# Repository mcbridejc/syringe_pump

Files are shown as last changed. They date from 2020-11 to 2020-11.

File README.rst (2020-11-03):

================
DIY Syringe Pump
================

A simple, cheap syringe pump designed for pumping controlled volumes of fluid
onto and off of the PurpleDrop_. It's built from 3D printed custom parts and
off-the-shelf parts from ServoCity_, with a Pololu Tic stepper controller so
that it can be plugged easily into a USB port and controlled using the drivers
from Pololu.

This design was inspired by C.A. Varnon's `open source design <http://cavarnon.com/syringepump>`_.
It's very similar, but a bit more compact, being designed for a smaller stepper
motor and smaller syringe.

The main disadvantage of the design is that there is a significant backlash,
which leads to hysteresis when changing the direction of pumping. For my
application, this is not much of a concern, as each pump will operate in
only one direction. However, it may be an issue in some cases. I think it may
be correctable with the addition of a tension spring between the end-plate and
the "sled", but I haven't tested this. It's probably necessary to get a longer
U-channel in order to accomodate the spring and still be able to actuate the full
plunger depth.

The total cost of parts is about $100.

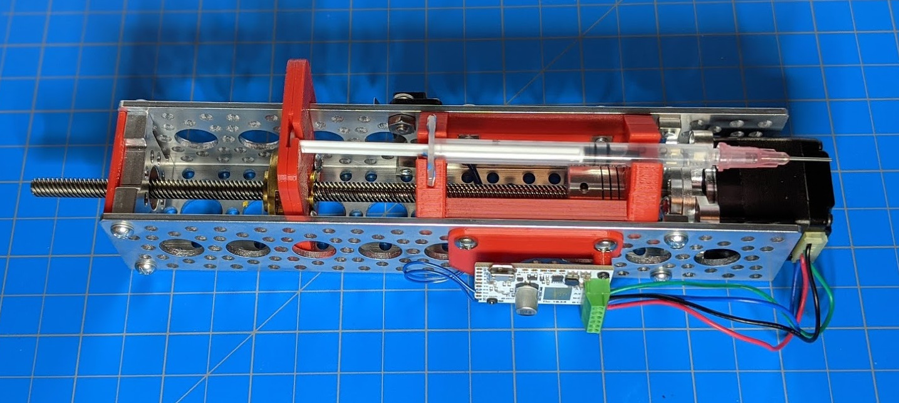
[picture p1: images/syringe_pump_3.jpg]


Control Software
================

The Tic board provides a number of interfaces for controlling the stepper motor.
I use the USB interface, and the pololu provided command line driver.

See the `User's Guide <https://www.pololu.com/docs/0J71>`__ for more details on how
to install, and the available control interface options. I control the motors with
a python wrapper library that runs `ticcmd` via `subprocess` calls. If you have
multiple controllers plugged in, it's easy to control the correct one using their
serial number.

Components
==========

Servo City Parts
----------------

Everything but the stepper motor and the motor controller board is purchased
from servo city.

+----------------+---------------------------------------------------+
| Part Number    | Description                                       |
+================+===================================================+
| 545324_        | Side Tapped Pattern Mount D                       |
+----------------+---------------------------------------------------+
| 545424_        | Side Tapped Pattern Mount B                       |
+----------------+---------------------------------------------------+
| 555164_        | NEMA 11 Stepper Motor Mount                       |
+----------------+---------------------------------------------------+
| 585448_        | U-Channel (9-Hole, 7.5" length)                   |
+----------------+---------------------------------------------------+
| 545311_        | 6mm Lead Screw Nut, 0.77" pattern                 |
+----------------+---------------------------------------------------+
| 4002-0005-0006_| 5mm to 6mm Flexible Clamping Shaft Coupler        |
+----------------+---------------------------------------------------+
| 605630_        | SPDT Miniature Limit Switch with Lever            |
+----------------+---------------------------------------------------+
| 605627_        | Limit Switch Mount D                              |
+----------------+---------------------------------------------------+
| 585474_        | Single Screw Plate (24 pack)                      |
+----------------+---------------------------------------------------+
| 3501-0606-0350_| 350mm 6mm Lead Screw                              |
+----------------+---------------------------------------------------+
| 632176_        | 6-32 0.25" Pan Head Screws                        |
+----------------+---------------------------------------------------+
| 632180_        | 6-32 0.375" Pan Head Screws                       |
+----------------+---------------------------------------------------+
| 632184_        | 6-32 0.5" Pan Head Screws                         |
+----------------+---------------------------------------------------+

The lead screw has to be cut, and one is long enoguh to make two pumps.
It is steel. I cut it in half with a dremel and a cutoff wheel.

Pololu Parts
------------

+----------------+--------------------------------------------+
| Part Number    | Description                                |
+================+============================================+
| 1205_          | Stepper Motor: Bipolar, 200 Steps/Rev,     |
|                | 28×32mm, 3.8V, 0.67 A/Phase                |
+----------------+--------------------------------------------+
| 3133_          | Tic T824 USB Multi-Interface Stepper Motor |
|                | Controller                                 |
+----------------+--------------------------------------------+

.. _PurpleDrop: https://github.com/uwmisl/purpledrop/
.. _ServoCity: www.servocity.com
.. _545324: https://www.servocity.com/nema-11-stepper-motor-mount/
.. _555164: https://www.servocity.com/side-tapped-pattern-mount-d/
.. _545424: https://www.servocity.com/side-tapped-pattern-mount-b/
.. _585448: https://www.servocity.com/7-50-aluminum-channel/
.. _545311: https://www.servocity.com/6mm-lead-screw-nut-0-770-pattern/
.. _4002-0005-0006: https://www.servocity.com/5mm-to-6mm-flexible-clamping-shaft-coupler/
.. _605630: https://www.servocity.com/spdt-miniature-limit-switch-with-lever-2-pack/
.. _605627: https://www.servocity.com/limit-switch-mount-d-2-pack/
.. _585474: https://www.servocity.com/single-screw-plate-24-pack/
.. _3501-0606-0350: https://www.servocity.com/350mm-6mm-lead-screw/
.. _632176: https://www.servocity.com/6-32-zinc-plated-steel-pan-head-screw-25-pack-0-250-1-4/
.. _632180: https://www.servocity.com/0-375-3-8-l-x-6-32-zinc-plated-steel-pan-head-screw-25-pack/
.. _632184: https://www.servocity.com/0-500-1-2-6-32-zinc-plated-steel-pan-head-screw-25-pack/
.. _1205: https://www.pololu.com/product/1205
.. _3133: https://www.pololu.com/product/3133

3D Printed Parts
----------------

The 3D printed parts are designed in Fusion 360. They can all be printed easily
on an FDM printer without support material. Some of them are designed to be
printed in two halves, and glued together with CA glue.

The 3D printed parts are designed for use with BSTEAN 1mL syringes, which I
bought on amazon along with blunt needles to attach to it. These syringes have
a 6.65mm outer diameter, and I suspect that many brands of 1mL syringe will
fit, but I haven't tested others. The 3D printed parts may need some tweaking
to use with different size syringes.

For mounting the Tic controller board to the mount, I drilled holed in the
printed part, and used self tapping screws to mount. Self tapping screws into
PLA isn't an amazingly strong solution -- and don't overtighten them! -- but
it has been fine.

Sled
~~~~

+--------------------+------------------------------------------------+
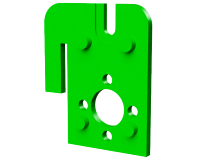
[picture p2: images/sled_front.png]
|        | Design Files:                                  |
|                    |                                                |
|                    | - `STL <models/sled_front.stl>`__              |
|                    | - `STEP <models/sled_front.step>`__            |
+--------------------+------------------------------------------------+
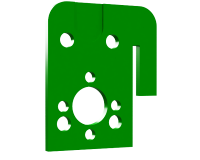
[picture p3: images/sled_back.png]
|         | Design Files:                                  |
|                    |                                                |
|                    | - `STL <models/sled_back.stl>`__               |
|                    | - `STEP <models/sled_back.step>`__             |
+--------------------+------------------------------------------------+

Cradle
~~~~~~

+--------------------+------------------------------------------------+
|  Side A                                                             |
+--------------------+------------------------------------------------+
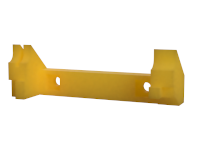
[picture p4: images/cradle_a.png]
|          | Design Files:                                  |
|                    |                                                |
|                    | - `STL <models/cradle_a.stl>`__                |
|                    | - `STEP <models/cradle_a.step>`__              |
+--------------------+------------------------------------------------+
|  Side B                                                             |
+--------------------+------------------------------------------------+
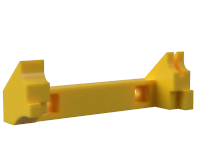
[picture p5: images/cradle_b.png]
|          |  Design Files:                                 |
|                    |                                                |
|                    | - `STL <models/cradle_b.stl>`__                |
|                    | - `STEP <models/cradle_b.step>`__              |
+--------------------+------------------------------------------------+

Endplate
~~~~~~~~

+--------------------+------------------------------------------------+
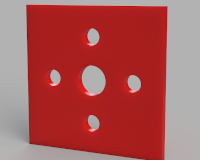
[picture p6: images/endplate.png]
|          | Design Files:                                  |
|                    |                                                |
|                    | - `STL <models/endplate.stl>`__                |
|                    | - `STEP <models/endplate.step>`__              |
+--------------------+------------------------------------------------+

Controller Mount
~~~~~~~~~~~~~~~~

+--------------------+------------------------------------------------+
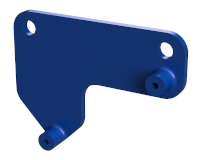
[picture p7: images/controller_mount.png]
|  | Design Files:                                  |
|                    |                                                |
|                    | - `STL <models/controller_mount.stl>`__        |
|                    | - `STEP <models/controller_mount.step>`__      |
+--------------------+------------------------------------------------+








Detailed Images
################

Assembled sled:

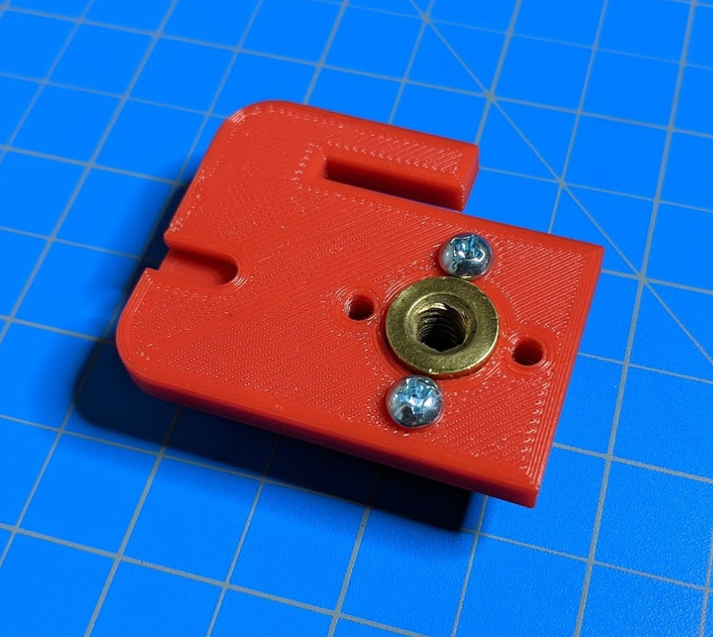
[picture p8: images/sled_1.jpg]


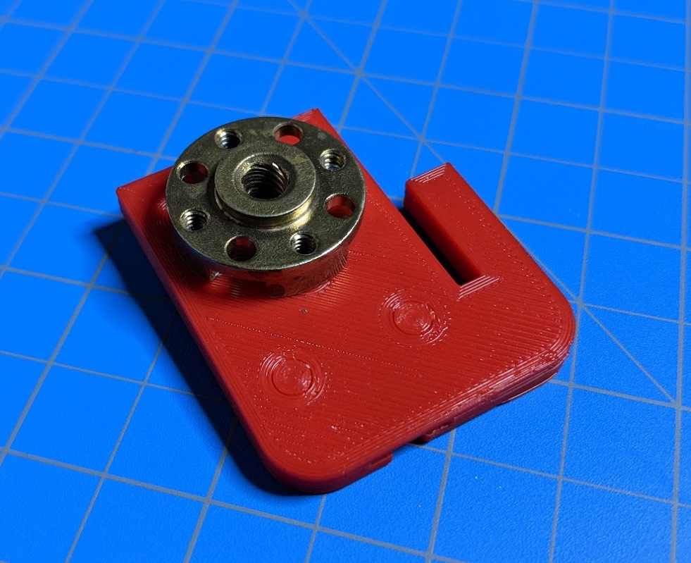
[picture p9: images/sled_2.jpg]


Full Assembly:

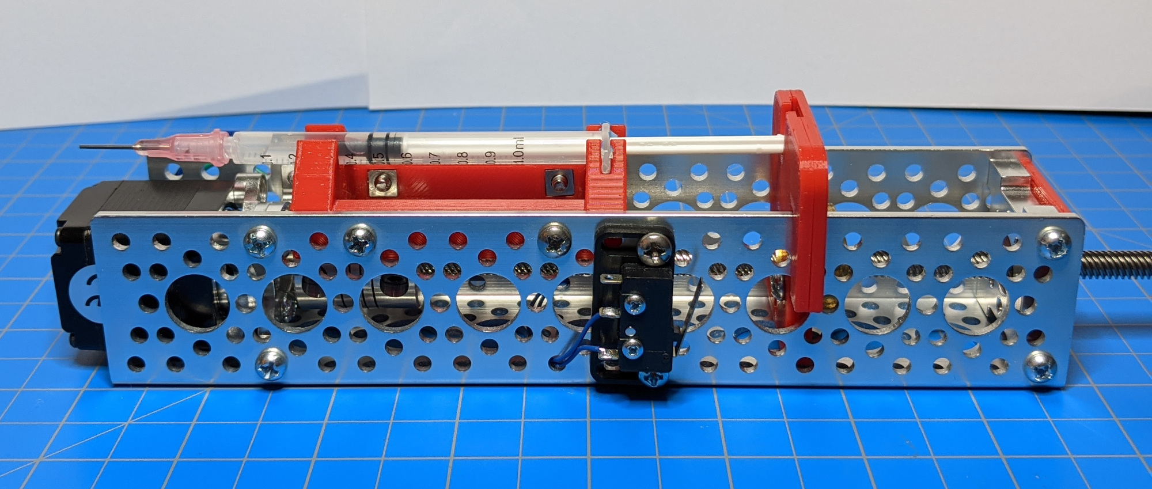
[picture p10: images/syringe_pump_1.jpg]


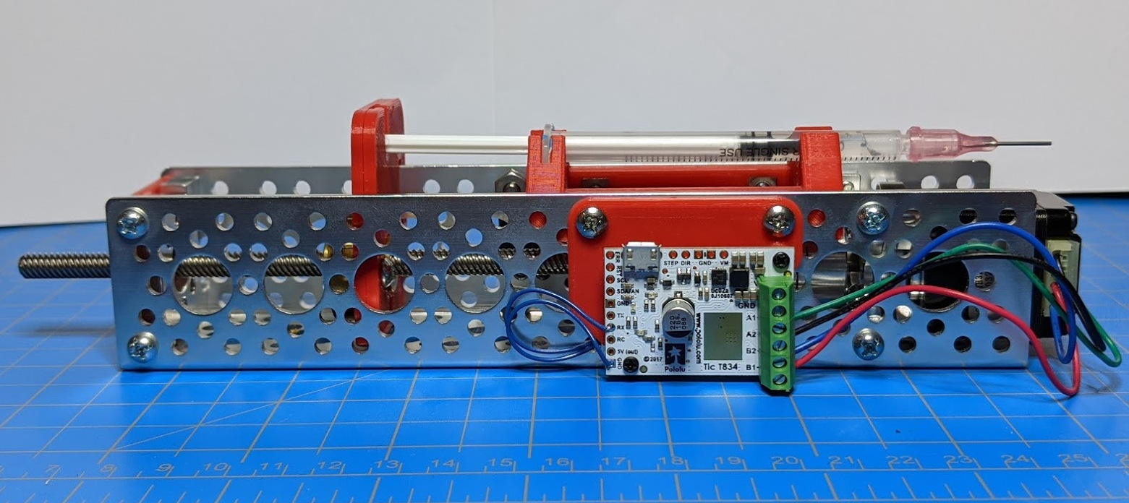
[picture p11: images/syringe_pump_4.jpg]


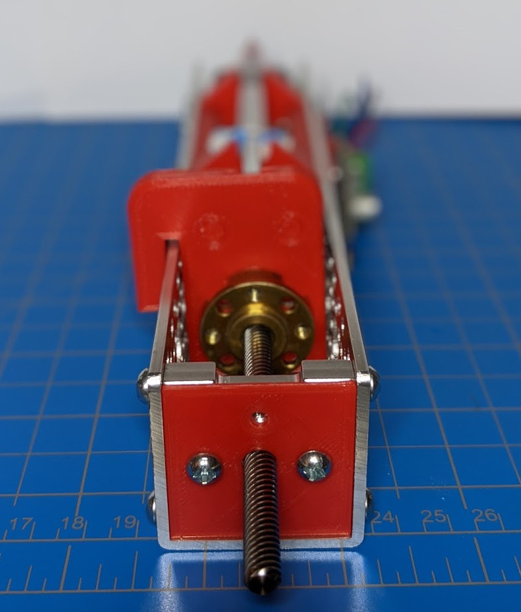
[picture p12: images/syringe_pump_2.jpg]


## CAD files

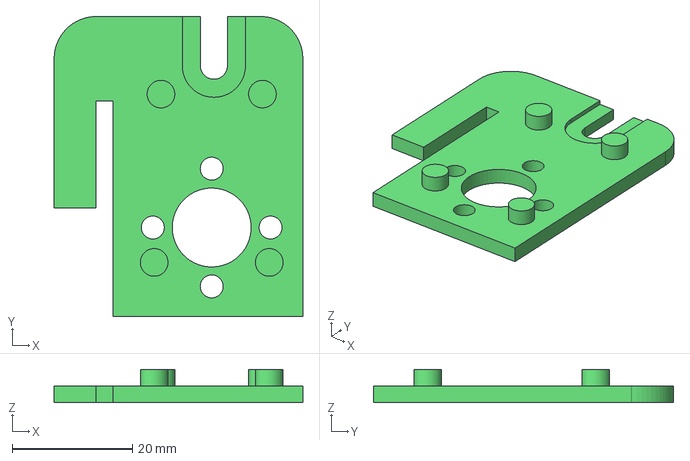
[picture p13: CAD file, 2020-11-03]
models/sled_front.step
41.3 x 49.8 x 5.50 mm

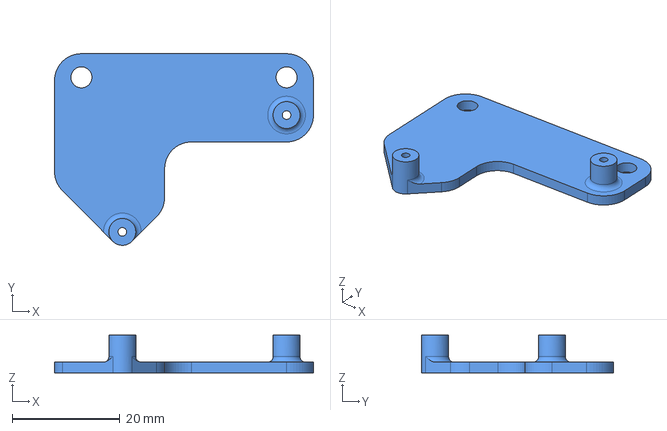
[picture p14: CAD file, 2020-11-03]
models/controller_mount.step
48.1 x 35.6 x 7.00 mm

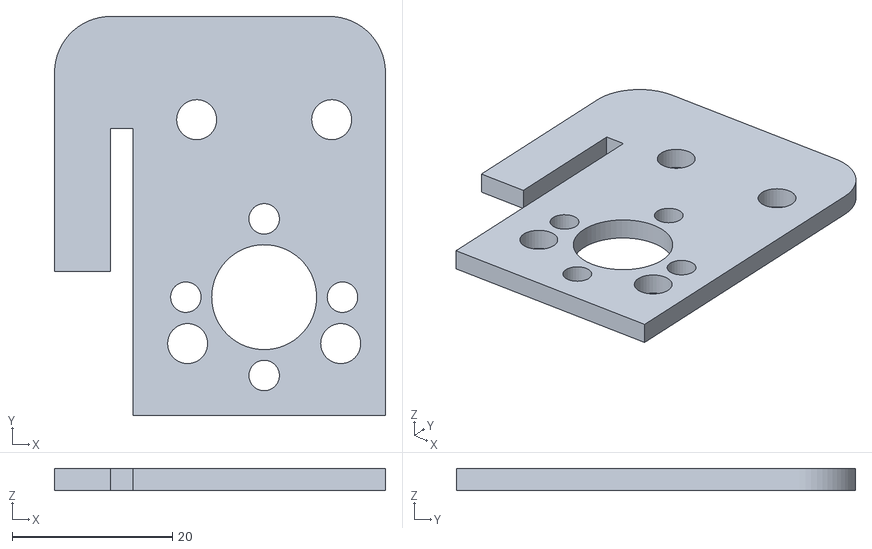
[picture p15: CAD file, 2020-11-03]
models/seld_back.stl
41.3 x 49.8 x 2.75

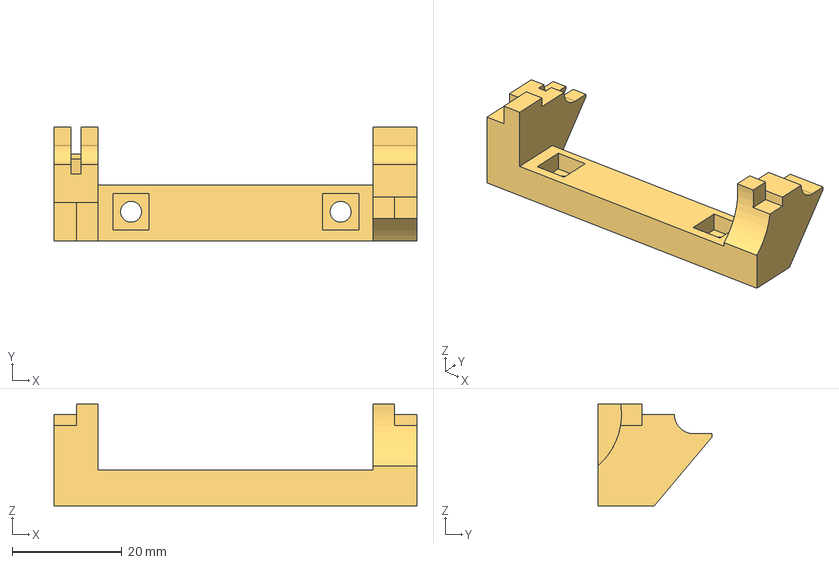
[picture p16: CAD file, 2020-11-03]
models/cradle_a.step
66.0 x 20.7 x 18.5 mm

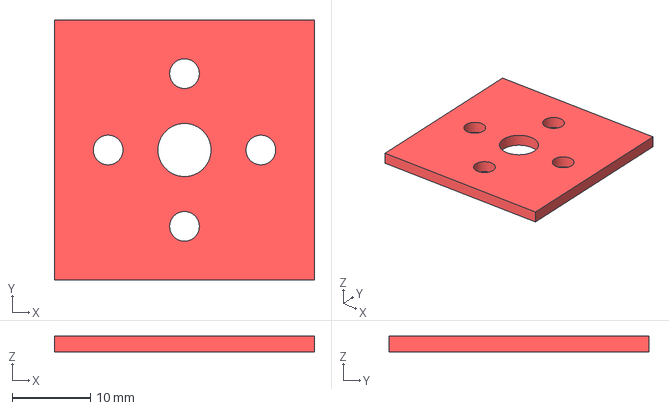
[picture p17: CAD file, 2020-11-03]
models/endplate.step
33.3 x 33.3 x 2.00 mm

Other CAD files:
models/sled_back.step
models/cradle_b.step
models/controller_mount.stl
models/cradle_a.stl
models/cradle_b.stl
models/endplate.stl
models/sled_front.stl
